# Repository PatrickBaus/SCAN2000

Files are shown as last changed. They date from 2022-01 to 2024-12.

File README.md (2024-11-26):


# Keithley 2000-SCAN SSR Replacement

This repository contains the KiCAD PCB project files for a [Keithley Model 2000-SCAN](https://download.tek.com/manual/2000SCAN-901-01_F-Jan-2014.pdf) replacement card. It uses solid-state relays instead of mechanical relays. See [below](#introduction) for a list of compatible devices. The design files can be found on the [releases](../../releases) page.

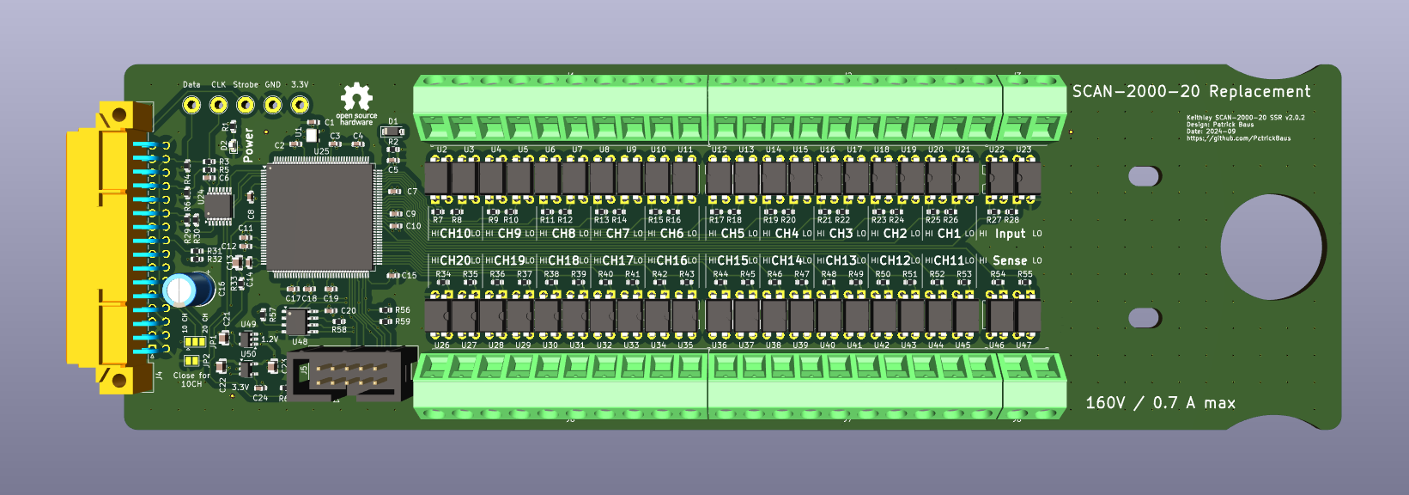
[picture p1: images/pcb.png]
SCAN2000 board


## Contents
- [Introduction](#introduction)
- [Design Files](#design-files)
- [Installation](#installation)
- [Accesories](#accesories)
- [Related Repositories](#related-repositories)
- [Versioning](#versioning)
- [License](#license)

## Introduction
The design is the successor of the SCAN2000 STM32 board previously released as [v1.x](https://github.com/PatrickBaus/SCAN2000/tree/v1). Instead of an STM32 microcontroller it uses an [iCE40](https://www.latticesemi.com/iCE40) FPGA to emulate the shift registers found on the 10 channel [Model 2000-SCAN](https://download.tek.com/manual/2000SCAN-901-01_F-Jan-2014.pdf) card and is also capable of decoding the protcol used by the 20-channel [Model 2000-SCAN-20](https://download.tek.com/manual/2000-20-901-01C_Jul2003_Instruction.pdf). The advantage of the FPGA is that the shift registers are implemented in hardware. The protocol spoken by the 10 channnel card requires freezing 24 bits clocked in _before_ the strobe bin is triggered, similar to the positive lookahead assertion of a [regular expression](https://en.wikipedia.org/wiki/Regular_expression). This is in stark contrast to typical protocols used by microcontrollers like, for example, [SPI](https://en.wikipedia.org/wiki/Serial_Peripheral_Interface) that uses a [chip select](https://en.wikipedia.org/wiki/Chip_select) control line to announce incoming data arriving _after_ the CS signal. A more detailed analysis of the problem can be found in the [doc/](doc/) folder.

The card was tested in a [Keithley DMM6500](https://www.tek.com/en/products/keithley/digital-multimeter/dmm6500) and a [Keithley Model 2002](https://www.tek.com/en/products/keithley/digital-multimeter/2002-series) in both configurations as a 10 channel and 20 channel card. The more recent [Keithley DMM6500](https://www.tek.com/en/products/keithley/digital-multimeter/dmm6500) supports both the older 10 channel [Model 2000-SCAN](https://download.tek.com/manual/2000SCAN-901-01_F-Jan-2014.pdf) and the newer [Model 2000-SCAN-20](https://download.tek.com/manual/2000-20-901-01C_Jul2003_Instruction.pdf) 20 channel scanner card. The same goes for the [Model 2000](https://www.tek.com/en/products/keithley/digital-multimeter/keithley-2000-series-6-digit-multimeter-scanning) and Model 2000-20. The Model 2000-20 is similar to the [Model 2000](https://www.tek.com/en/products/keithley/digital-multimeter/keithley-2000-series-6-digit-multimeter-scanning), but has a different firmware. The latest firmare of the [Model 2000](https://www.tek.com/en/products/keithley/digital-multimeter/keithley-2000-series-6-digit-multimeter-scanning) seems to support the 20 channel cards as well as suggested [here](https://www.eevblog.com/forum/circuit-studio/example-project-20-channel-solid-state-scan-card-for-k2000-dmm/msg3101128/#msg3101128). The [Model 2002](https://www.tek.com/en/products/keithley/digital-multimeter/2002-series) only supports 10 channel cards.

|DMM|Tested|Note|
|--|--|--|
|[DMM6500](https://www.tek.com/en/products/keithley/digital-multimeter/dmm6500)|:heavy_check_mark:|Works.|
|[2000](https://www.tek.com/en/products/keithley/digital-multimeter/keithley-2000-series-6-digit-multimeter-scanning)|:x:|Not tested, but should work. The latest firmware seems to support [20 channels](https://www.eevblog.com/forum/circuit-studio/example-project-20-channel-solid-state-scan-card-for-k2000-dmm/msg3101128/#msg3101128).|
|[2000-20](https://www.tek.com/en/products/keithley/digital-multimeter/keithley-2000-series-6-digit-multimeter-scanning)|:x:|Not tested, but should work.|
|[2010](https://www.tek.com/en/products/keithley/digital-multimeter/2010-series)|:heavy_check_mark:|Works, but only 10 channels cards are supported by the firmware.|
|[2001](https://www.tek.com/en/products/keithley/digital-multimeter/2001-series)|:x:|Not tested, but should work.|
|[2002](https://www.tek.com/en/products/keithley/digital-multimeter/2002-series)|:heavy_check_mark:|Works. Only 10 channels supported.|

## Design Files
The root folder contains the KiCAD files. The bill of materials can be found on the [releases](../../releases) page along with Gerber files for production.

## Installation
The source code for the FPGA and the installation instructions for the firmware can be found [here](https://github.com/PatrickBaus/SCAN2000_iCE40_Firmware). The FPGA source code must be written to the onboard SPI flash chip. One way to do so is to use an USB to SPI converter with an FT232H chip.

The SCAN2000 SSR board has two solder jumpers, ```JP1``` and ```JP2```. To enable only 10 channels close ```JP2``` and connect the two left pads of ```JP1``` together using a soldering iron. To enable 20 channel operation, leave ```JP2``` open and connect the two rightmost pads of ```JP1```.

The assembled card can then wired up and simply inserted into the multimeter. It will be supplied by the DMM through the Molex connector. To connect the scanner outputs to the, connect the screw terminals labeled ```Input``` to the DMM terminals labeled ```Input```. The same goes for the ```Sense``` terminals if operating in 4-wire mode.

## Accesories
The [Model 2000-SCAN](https://download.tek.com/manual/2000SCAN-901-01_F-Jan-2014.pdf) comes with four 10″ connectors that have a right angle 4 mm connector on one side and a tinned wire on the other. They are sold by Keithley as [CA-109A](https://download.tek.com/document/1KW-50660-1_Keithley_Test_Leads_Probes_Selector_Guide_100622.pdf) and are made by Mueller Electric. Their part numbers are [BU-0062-N-108-2 (red)](https://www.muellerelectric.com/products/bu-0062-n-108-2) and [BU-0062-N-108-0 (black)](https://www.muellerelectric.com/products/bu-0062-n-108-0). Keithley shortens the Mueller Electric parts to 10″. The same length is fine for this board as well.

## Related Repositories
See the following repositories for more information as these are part of the [design files](#design-files).

- [KiCad footprints](https://github.com/PatrickBaus/footprints.pretty)
- [KiCAD 3D models](https://github.com/PatrickBaus/footprints.3dshapes)
- [KiCAD schematic libraries](https://github.com/PatrickBaus/KiCad-libraries)

## Versioning
I use [SemVer](http://semver.org/) for versioning. For the versions available, see the [tags](../../tags) available for this repository.

- MAJOR versions in this context mean a breaking change to the external interface of the hardware like different connectors or functions.
- MINOR versions contain changes to the hardware that only affect the inner workings of the circuit, but otherwise the performance is unaffected.
- PATCH versions do not affect the schematics or invalidate older bill of materials. These changes may include updated components (to replace obsolete parts for example), an updated silkscreen, or fixed typos.

## License
This work is released under the CERN-OHL-W
See [https://ohwr.org/cern_ohl_w_v2.pdf](https://ohwr.org/cern_ohl_w_v2.pdf) or the included LICENSE file for more information.

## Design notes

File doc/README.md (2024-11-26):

# Keithley Model 2000-SCAN Serial Protocol
There are two versions of the scanner cards made by Keithley for their range of DMMs which are discussed here, the [Model 2000-SCAN](https://download.tek.com/manual/2000SCAN-901-01_F-Jan-2014.pdf) and the newer [Model 2000-SCAN-20](https://download.tek.com/manual/2000-20-901-01C_Jul2003_Instruction.pdf). Additionally there are the [Model 2001-SCAN](https://download.tek.com/manual/2001_SCAN_901_01C.pdf) and [Model 2001-TCSCAN](https://download.tek.com/manual/2001-TCSCAN-900-01A_April_2018.pdf). Both are 10 channel cards as well. The [Model 2001-SCAN](https://download.tek.com/manual/2001_SCAN_901_01C.pdf) has 8 relays and 2 SSRs for high speed multiplexing. The [Model 2001-TCSCAN](https://download.tek.com/manual/2001-TCSCAN-900-01A_April_2018.pdf) on the other hand has 9 channels and one reference junction for cold-junction compensated temperature measurements. The latter two will not be discussed here.

## Contents
- [Introduction](#introduction)
- [Model 2000-SCAN](#model-2000-scan)
- [Model 2000-SCAN-20](#model-2000-scan-20)
- [Exploring the Data Captures](#exploring-the-data-captures)

## Introduction
The schematics of the [Model 2000-SCAN](https://download.tek.com/manual/2000SCAN-901-01_F-Jan-2014.pdf) and the [Model 2000-SCAN-20](https://download.tek.com/manual/2000-20-901-01C_Jul2003_Instruction.pdf) cards can both be found online. Do note that the latest version of the Model 2000-SCAN manual found on the Tektronix website does not contain the schematics any more. The last revision to contain them was Revision D from April 1999. Use a search engine to find it.

The ```Model 2000-SCAN``` and the ```Model 2000-SCAN-20``` use two different serial protocols. These were recorded for different multimeters with a [R&S RTH1004](https://www.rohde-schwarz.com/us/products/test-and-measurement/oscilloscopes/rs-scope-rider-handheld-oscilloscope_63493-156160.html) using its digital inputs. Additionally, different types of multimeters use different clock timings, which will also be discussed below.

## Model 2000-SCAN
The ```Model 2000-SCAN``` is the older 10 channel version of the scanner card and it works with all types of DMMs. The examples shown below were recorded with a [DMM6500](https://www.tek.com/en/products/keithley/digital-multimeter/dmm6500) and a [Model 2002](https://www.tek.com/en/products/keithley/digital-multimeter/2002-series) as the host machine.

### Commands
The data communication between the card and the host device requires three data lines. The ```CLK``` line (recorded on channel ```D0```), the ```DATA``` line (```D2```) and a ```LATCH```/```STROBE``` line (```D1```). For the 10 channel card the DMM transfers 2 blocks of 3 bytes of data. It pulls the ```LATCH``` line ```high``` after each block. The first block sets or unsets all relays as required, the second block turns off the relay coils. In case of the [Model 2002](https://www.tek.com/en/products/keithley/digital-multimeter/2002-series) the ```CLK``` and ```DATA``` line idle ```high``` and only the ```LATCH``` line idles ```low```.
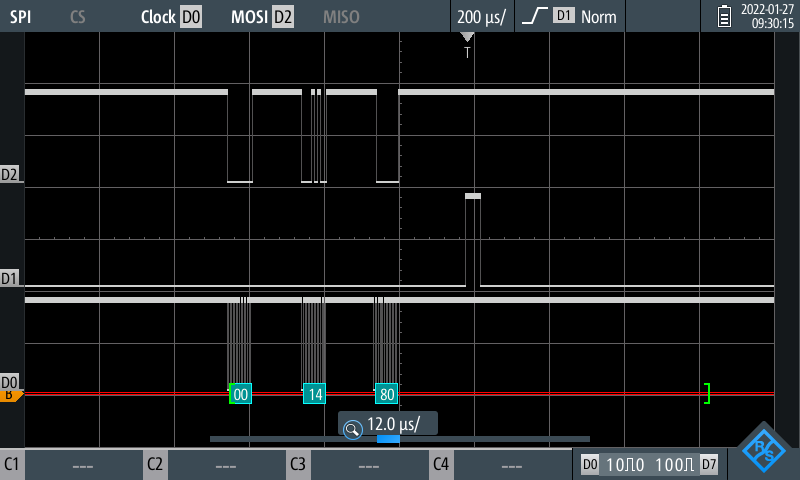
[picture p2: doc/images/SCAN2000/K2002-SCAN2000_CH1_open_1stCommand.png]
Model 2000-SCAN DMM6500 opening CH1


The [DMM6500](https://www.tek.com/en/products/keithley/digital-multimeter/dmm6500) uses a different scheme where all data lines idle ```low``` as can be seen here.
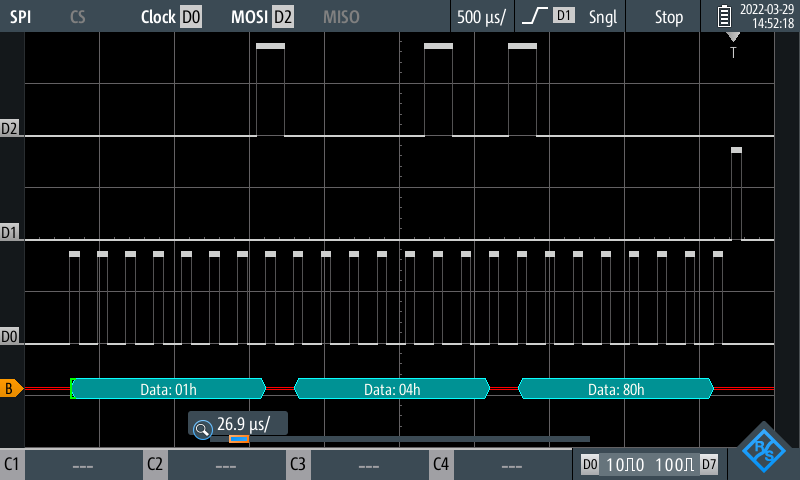
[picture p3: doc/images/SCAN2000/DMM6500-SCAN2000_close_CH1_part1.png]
Model 2000-SCAN DMM6500 closing CH1


The protocol itself is a series bits where each bit correspondes to a relay coil either being turned on or off. This is due to the nature of the 2-coil latching relays (```Panasonic TQ2E-L2-5V```). Each of those coils is responsible for either closing the relay or opening it. 10 relays plus 1 relay to switch between 4W mode and 2W mode requires 22 bits to control, hence two fewer than the 24 bits sent.

The decoded protocol is shown here and can also verified using the schematic schown in the manual.

```mermaid
---
title: "2000-SCAN protocol"
---
packet-beta
0: "7⮝"
1: "8⮟"
2: "8⮝"
3: "9⮟"
4: "9⮝"
5: "10⮝"
6: "10⮟"
7: "X"
8: "5⮝"
9: "5⮟"
10: "X"
11: "4W⮟"
12: "4W⮝"
13: "6⮟"
14: "6⮝"
15: "7⮟"
16: "1⮟"
17: "1⮝"
18: "2⮟"
19: "2⮝"
20: "3⮟"
21: "3⮝"
22: "4⮟"
23: "4⮝"
```

```⮟``` means closing the channel, ```⮝``` means opening the channel, ```X``` means do-not-care bit. The do-not-care bits have no meaning as those pins of the latches on the PCB are not connected. See pin Q8 of U101 (bit 7) and pin Q3 of U102 (bit 10). The do-not-care bits are typically set, but this is not required by the hardware.

As mentioned above, once the relay configuration is sent, the DMM then sends a series of zeroes to turn off the current to the relay coils. The [Model 2002](https://www.tek.com/en/products/keithley/digital-multimeter/2002-series) waits roughly ```2.8 ms``` between the datablock blocks

![Model 2000-SCAN K2002 timing between data blocks](images/SCAN2000/K2002-SCAN2000_command_interval.png)

while the [DMM6500](https://www.tek.com/en/products/keithley/digital-multimeter/dmm6500) waits ```3.8 ms``` for the relay to actuate.

![Model 2000-SCAN DMM6500 timing between data blocks](images/SCAN2000/DMM6500-SCAN2000_command_interval.png)

### Clock Speed
The most striking difference between the [DMM6500](https://www.tek.com/en/products/keithley/digital-multimeter/dmm6500) and the [Model 2002](https://www.tek.com/en/products/keithley/digital-multimeter/2002-series) is the data rate at which the signals are transferred. The clock frequency used by the [Model 2002](https://www.tek.com/en/products/keithley/digital-multimeter/2002-series) is ```2 MHz```

![Model 2000-SCAN K2002 SCLK frequency](images/SCAN2000/K2002-SCAN2000_CLK_timing.png)

while the  [DMM6500](https://www.tek.com/en/products/keithley/digital-multimeter/dmm6500) uses a clock speed of ```100 kHz```

![Model 2000-SCAN DMM6500 SCLK frequency](images/SCAN2000/DMM6500_CLK_timing.png)

The reason for the faster clock of the [Model 2002](https://www.tek.com/en/products/keithley/digital-multimeter/2002-series) is simple. The bus of the [Model 2002](https://www.tek.com/en/products/keithley/digital-multimeter/2002-series) is used by multiple devices all talking on the same wire, which can be seen here:

![Model 2000-SCAN K2002 second device sending data](images/SCAN2000/K2002-SCAN2000_2commands_second_transmitter_all_annotated.png)

In yellow there is a data packet for another device being transferred on the bus (```D0``` and ```D2```), but there is no ```LATCH``` line (```D1```) activity. Later there more data packets coming in and circled in red the two ```LATCH``` signals (```D1```) can be seen. There are are at least two more devices active on that bus. One transfers at ```1 MHz``` clock speed

![Model 2000-SCAN K2002 clockspeed of the  second device](images/SCAN2000/K2002-SCAN2000_CLK_timing_second_transmitter.png)

The other one is even slower and shows up as seemingly rogue bits on the ```CLK```/```D0``` line.

![Model 2000-SCAN K2002 additional devices on the bus](images/SCAN2000/K2002-SCAN2000_second_transmitter.png)

The image above shows both of the two other devices on the bus. There is activity on the ```CLK```/```D0``` line with two different clock intervals. The lone pulse on the right side is the slow third device. This third device is the reason why using a standard microcontroller is not possible, like in [v1.x](https://github.com/PatrickBaus/SCAN2000/tree/v1) of the scanner card that used an STM32 microcontroller. MCUs are aligned to a fixed number of clock cycles when reading a bus using their hardware peripherals. The extra clock pulse of the slow transmitter causes the hardware controller to desync at random intervals. Sampling the bus in software instead of the hardware interface is not feasable as well as the bus too fast at ```2 MHz```. Using the latches of the original Keithley design, this is not a problem, as the last 24 bits before a ```LATCH``` signal comes in are stored in the latch. Using an FPGA for this design allows to mimic the latches while allowing to switch between the [Model 2000-SCAN protocol](#commands) and the [Model 2000-SCAN-20 protocol](#commands-1) without changing the hardware.

## Model 2000-SCAN-20
The [Model 2000-SCAN-20](https://download.tek.com/manual/2000-20-901-01C_Jul2003_Instruction.pdf) is a more modern card which is only supported by the latest firmware of the [Model 2000](https://www.tek.com/en/products/keithley/digital-multimeter/keithley-2000-series-6-digit-multimeter-scanning) DMM and the [DMM6500](https://www.tek.com/en/products/keithley/digital-multimeter/dmm6500). The examples shown below were recorded with a [DMM6500](https://www.tek.com/en/products/keithley/digital-multimeter/dmm6500) as the host machine.

### Commands
The data communication also requires three data lines like the 10-channel card. The ```CLK``` line (```D0```), the ```DATA``` line (```D2```) and a ```LATCH```/```STROBE``` line (```D1```). The protocol is a bit more straight forward, even bits disconnect the relay, odd bits connect the relay. The 20 relays plus 1 relay for the 4W mode require 42 bits. This is being sent as 6 bytes.

```mermaid
---
title: "2000-SCAN-20 protocol"
---
packet-beta
0-1: "11"
2-3: "12"
4-5: "13"
6-7: "14"
8-9: "15"
10-11: "16"
12-13: "17"
14-15: "18"
16-17: "19"
18-19: "20"
20-21: "1"
22-23: "2"
24-25: "3"
26-27: "4"
28-29: "5"
30-31: "6"
32-33: "7"
34-35: "8"
36-37: "9"
38-39: "10"
40-41: "4W"
42-47: "X"
```

For example closing CH1 is sent as two blocks of ```0x00``` ```0x00``` ```0x00``` ```0x20``` ```0x00``` ```0x00``` (bit 21 is set) and ```0x00``` ```0x00``` ```0x00``` ```0x00``` ```0x00``` ```0x00```. The second block turns all relay coils off as discussed above.

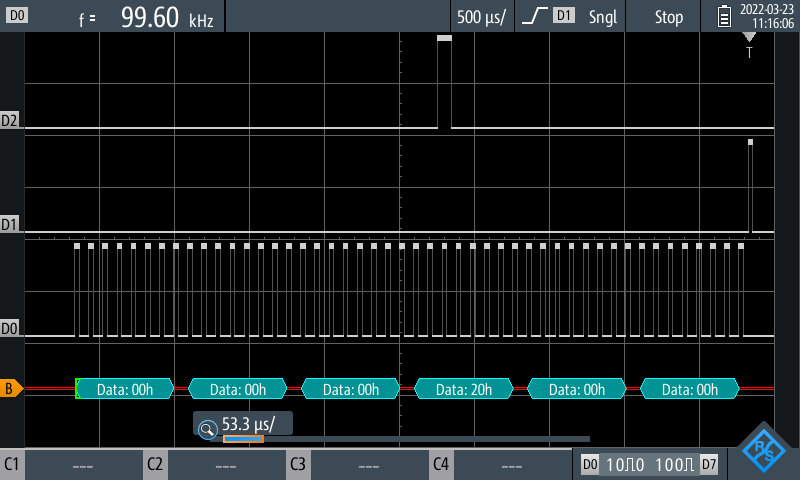
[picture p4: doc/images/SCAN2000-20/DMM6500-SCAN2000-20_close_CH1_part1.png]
Model 2000-SCAN-20 DMM6500 closing CH1, first block
 and

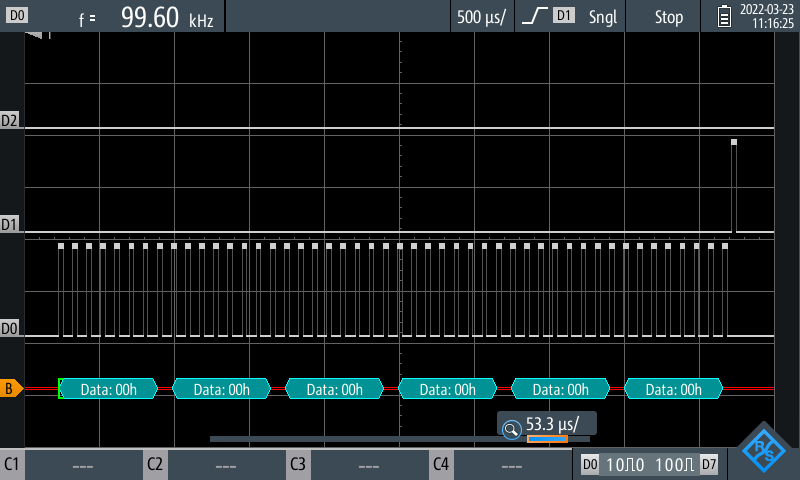
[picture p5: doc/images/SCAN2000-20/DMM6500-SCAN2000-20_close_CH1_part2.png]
Model 2000-SCAN-20 DMM6500 closing CH1, second block


The second block is sent after a delay of ```3.8 ms```.

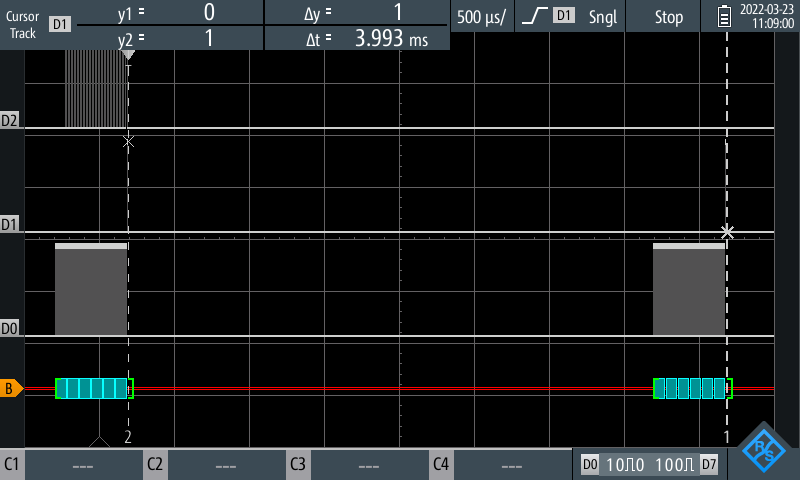
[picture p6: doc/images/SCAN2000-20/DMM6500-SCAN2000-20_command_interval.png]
Model 2000-SCAN-20 DMM6500 timing between data blocks


### Clock Speed
The [DMM6500](https://www.tek.com/en/products/keithley/digital-multimeter/dmm6500) clocks this bus at ```100 kHz``` just like the 10-channel version.

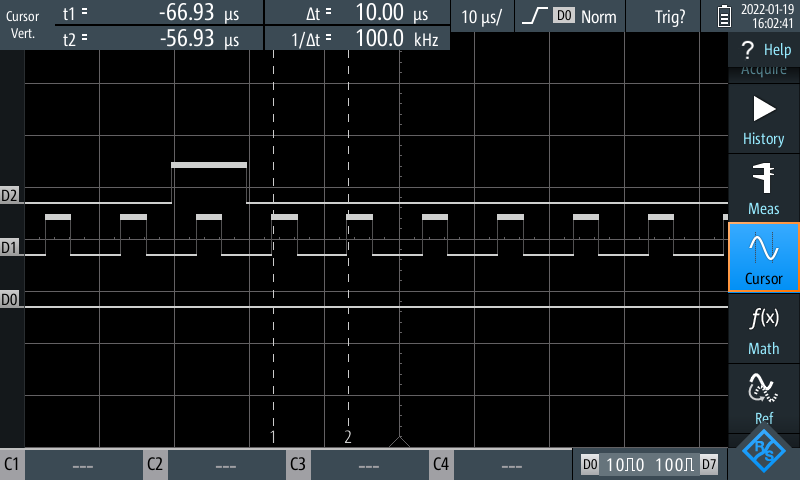
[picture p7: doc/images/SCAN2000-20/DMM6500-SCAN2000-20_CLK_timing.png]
Model 2000-SCAN-20 DMM6500 SCLK frequency


Do note, the ```CLK``` line is input channel ```D1``` and ```STROBE``` is ```D1``` in this capture.

## Exploring the Data Captures
This repository not only provides screen captures, but also the raw data obtained using the [R&S RTH1004](https://www.rohde-schwarz.com/us/products/test-and-measurement/oscilloscopes/rs-scope-rider-handheld-oscilloscope_63493-156160.html). This data can be found in the [plots/](plots/) directory as [csv files](https://en.wikipedia.org/wiki/Comma-separated_values) and can be plotted using your own plotter or the example [Python Matplotlib](https://matplotlib.org/) [script](plots/plotter.py) provided. This section shows how to install the script.

### Installing Dependencies
These instructions assume a Linux Bash shell and Python already installed on the system. Type or copy the following commands into a shell in the [doc/plots/](plots/) directory.

```bash
python -m venv env/
source env/bin/activate
pip install - r requirements.txt
```

### Running the Script
The plot script can now be executed using the following commands run inside the [doc/plots/](plots/) directory
```bash
source env/bin/activate
./plotter.py <plot_file>
```

The `source env/bin/activate` line can omitted if the virtual environment has already been activated. The ```<plot_file>``` must be any of the Python files provided in the [doc/plots/SCAN2000](plots/SCAN2000) or [doc/plots/SCAN2000-20](plots/SCAN2000-20) subdirectories, for example
```bash
./plotter.py SCAN2000/K2002-SCAN2000_commands_and_second_transmitter.py
```

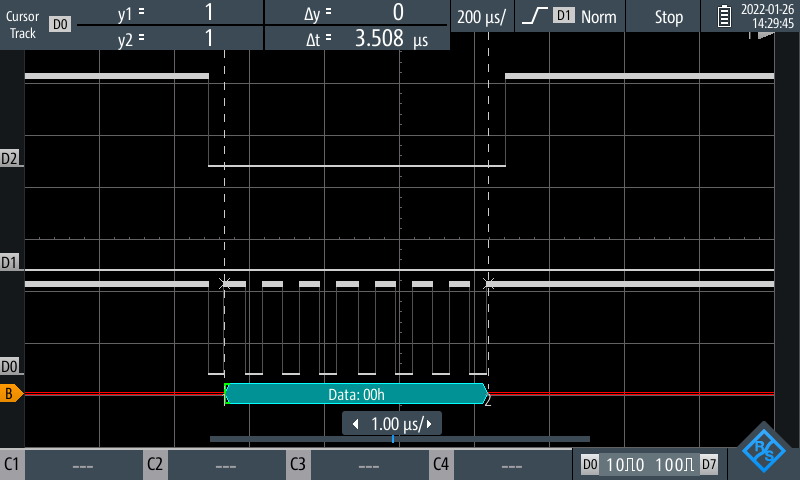
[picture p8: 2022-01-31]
doc/images/SCAN2000/K2002-SCAN2000_CLK_timing.png

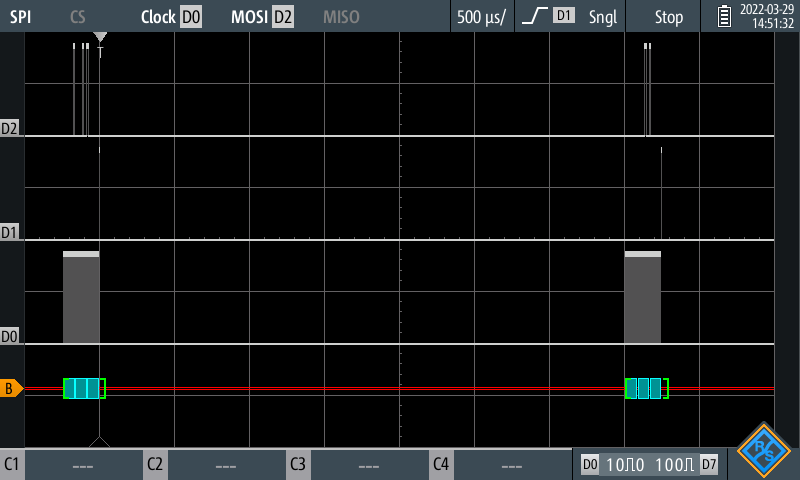
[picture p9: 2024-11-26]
doc/images/SCAN2000/DMM6500-SCAN2000_close_CH1.png

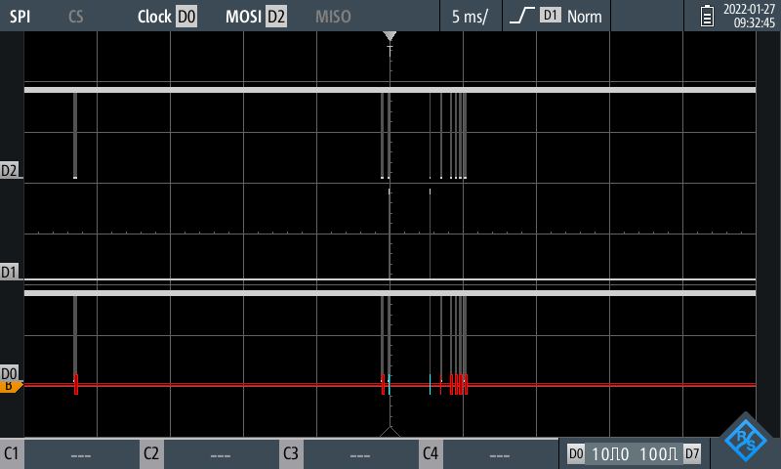
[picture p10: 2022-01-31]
doc/images/SCAN2000/K2002-SCAN2000_2commands_second_transmitter_all.png

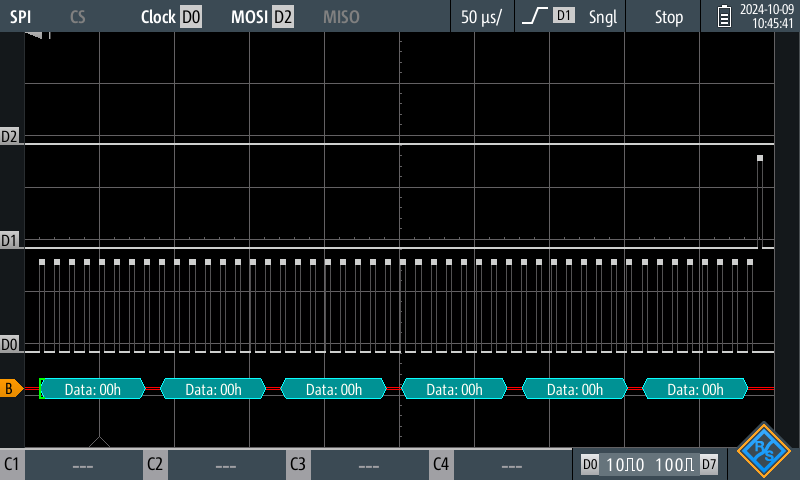
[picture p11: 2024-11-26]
doc/images/SCAN2000-20/DMM6500-SCAN2000-20_close_CH2_4W_part2.png

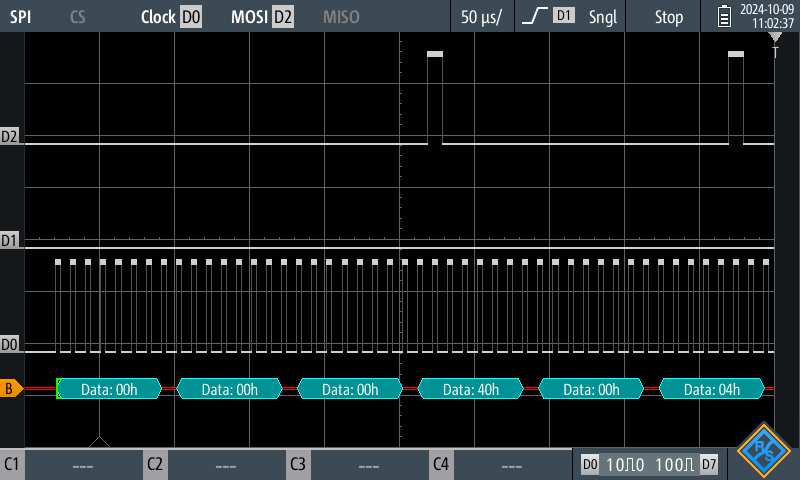
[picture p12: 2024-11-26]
doc/images/SCAN2000-20/DMM6500-SCAN2000-20_open_CH2_4W_close_CH10_4W_part1.png

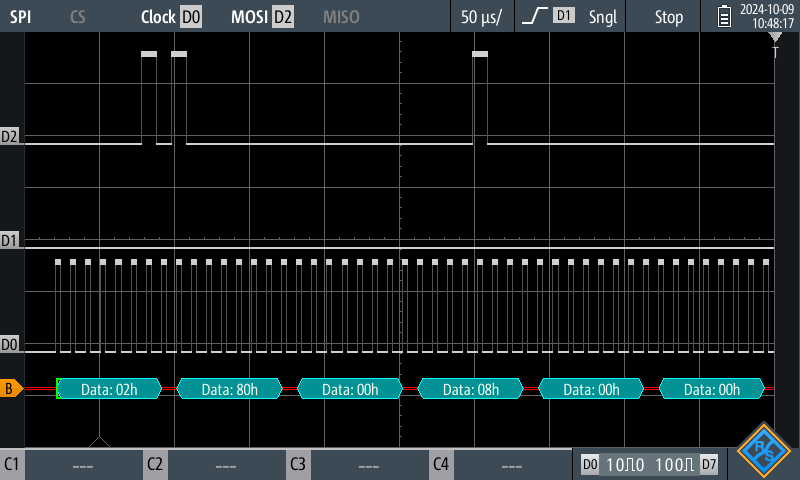
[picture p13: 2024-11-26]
doc/images/SCAN2000-20/DMM6500-SCAN2000-20_close_CH10_4W_part1.png

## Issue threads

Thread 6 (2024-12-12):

### ISSUE TITLE
2.0.2 Gerber archive doesn't contain internal layers

### ISSUE THREAD

**Issue by reykada** [PatrickBaus/SCAN2000#6]
I just realized it after 2-layer PCBs ordered and arrived when I started to assembly, luckily only FPGA and few capacitors were soldered only.

**Comment by PatrickBaus** [comment]
Oh, you are absolutely right. I am so sorry. I have added the missing layers to the CI and will release a new version immediately.

**Comment by reykada** [comment]
No worries, I had to check it myself before order PCBs. Thank you for the quick fix!

**Comment by PatrickBaus** [comment]
I have published version 2.0.3. As soon as the CI has built the files it should be available.

**Comment by reykada** [comment]
Cool, thanks for sharing the project!

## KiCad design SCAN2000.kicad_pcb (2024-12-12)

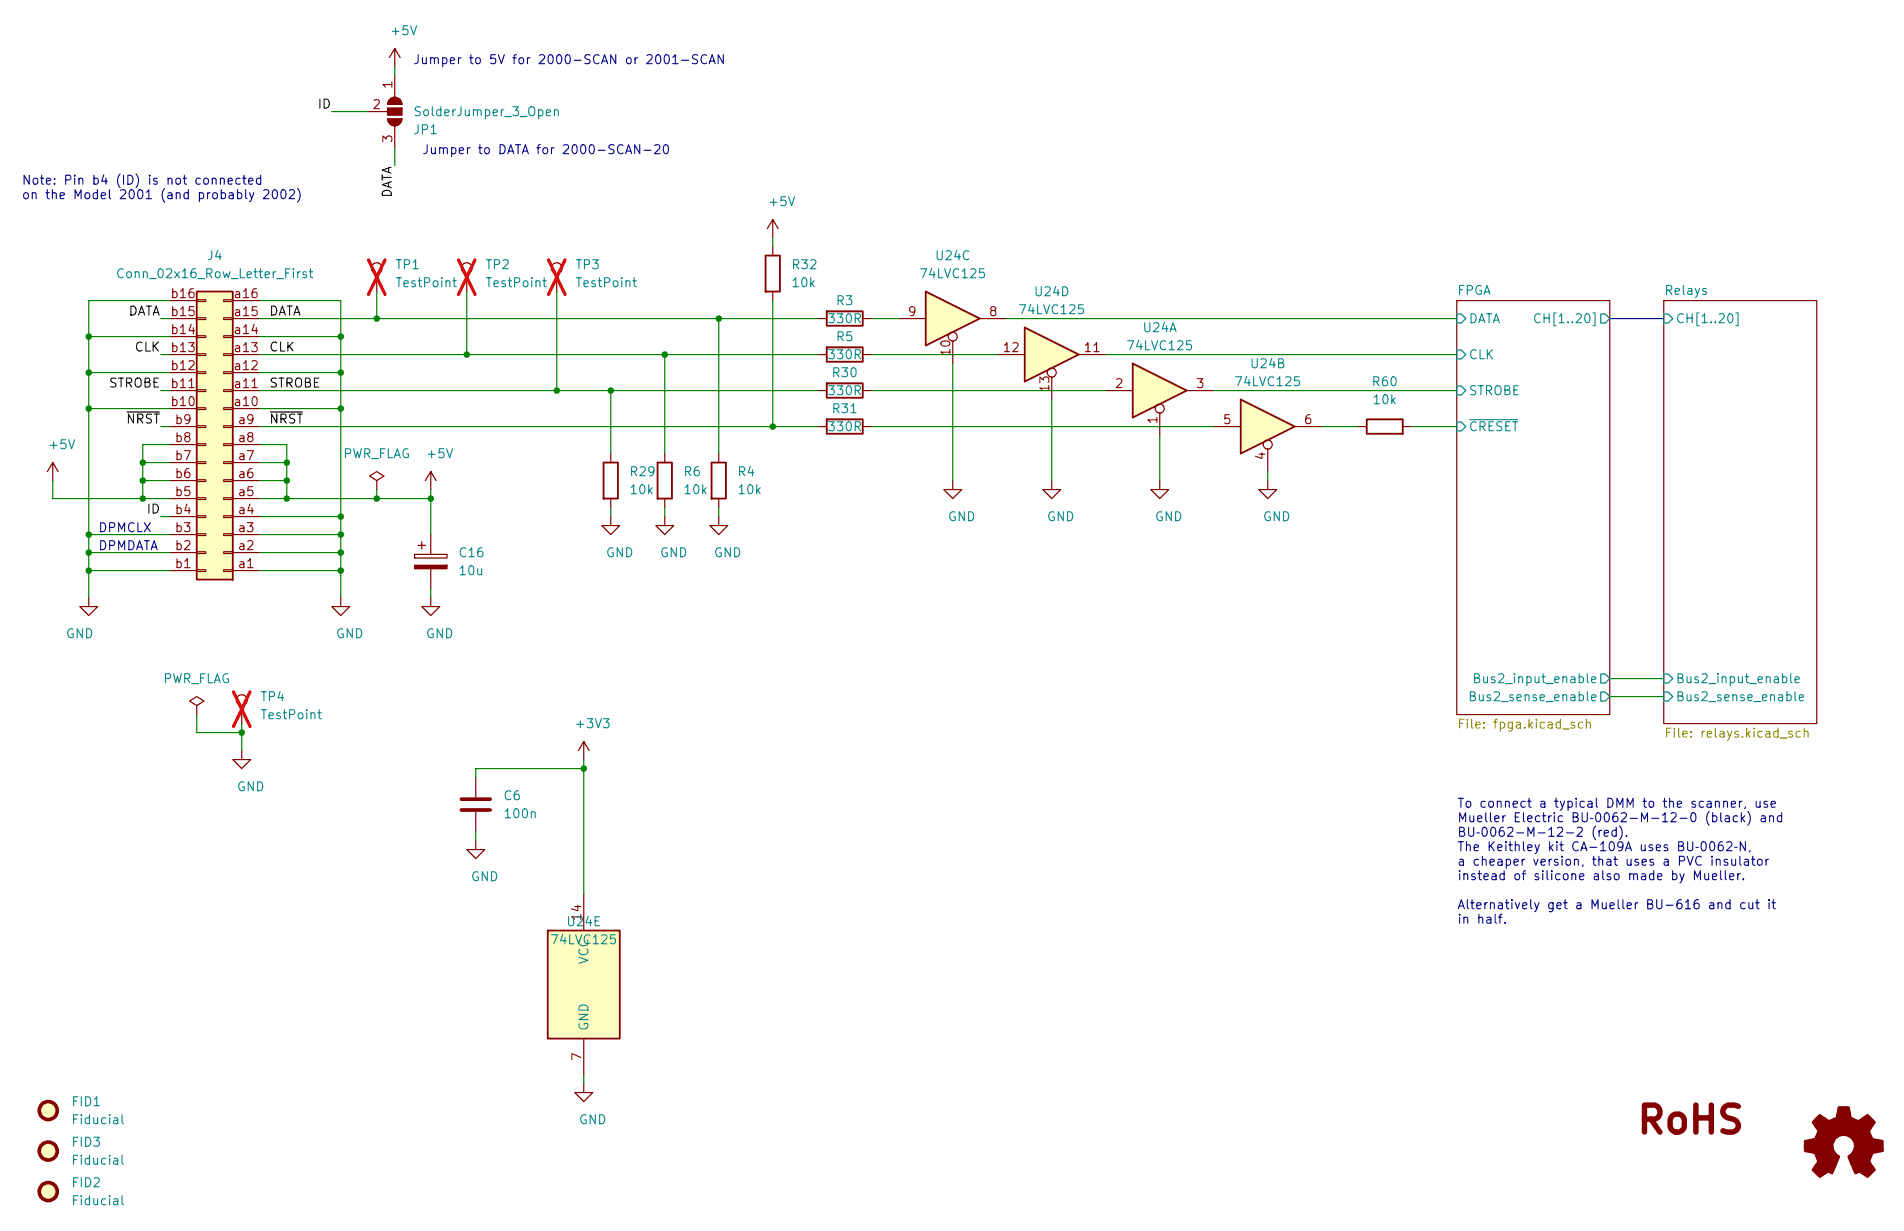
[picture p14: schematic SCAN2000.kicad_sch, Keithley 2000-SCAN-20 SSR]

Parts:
C6: 100n; C_0603_1608Metric
C16: 10u; CP_Radial_D6.3mm_P2.50mm
FID1, FID2, FID3: Fiducial; Fiducial_0.5mm_Mask1mm
J4: Conn_02x16_Row_Letter_First; DIN41612_B2_2x16_Male_Horizontal_THT; Digikey# 09272326804-ND
JP1: SolderJumper_3_Open; SolderJumper-3_P1.3mm_Open_Pad1.0x1.5mm
LOGO1: Logo_Open_Hardware_Small; OSHW-Logo_7.5x8mm_SilkScreen
R3, R5, R30, R31: 330R; R_0603_1608Metric
R4, R6, R29, R32, R60: 10k; R_0603_1608Metric
TP1, TP2, TP3, TP4: TestPoint; TestPoint_Loop_D2.60mm_Drill1.6mm_Beaded; not fitted
U24: 74LVC125; TSSOP-14_4.4x5mm_P0.65mm

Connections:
+3V3: C6.1, U24.14 (VCC); also elsewhere on the board
+5V: C16.1, J4.a5, J4.a6, J4.a7, J4.a8, J4.b5, J4.b6, J4.b7, J4.b8, JP1.1 (A), R32.1; also elsewhere on the board
/CLK: J4.a13, J4.b13, R5.2, R6.1, TP2.1
/DATA: J4.a15, J4.b15, JP1.3 (B), R3.2, R4.1, TP1.1
/FPGA/CLK: U24.11; also elsewhere on the board
/FPGA/DATA: U24.8; also elsewhere on the board
/FPGA/STROBE: U24.3; also elsewhere on the board
/FPGA/~CRESET: R60.2; also elsewhere on the board
/ID: J4.b4, JP1.2 (C)
/STROBE: J4.a11, J4.b11, R29.1, R30.2, TP3.1
/~NRST: J4.a9, J4.b9, R31.2, R32.2
GND: C6.2, C16.2, J4.a1, J4.a2, J4.a3, J4.a4, J4.a10, J4.a12, J4.a14, J4.a16, J4.b1, J4.b2, J4.b3, J4.b10, J4.b12, J4.b14, J4.b16, R4.2, R6.2, R29.2, TP4.1, U24.1, U24.4, U24.7 (GND), U24.10, U24.13; also elsewhere on the board
unnamed: R3.1, U24.9
unnamed: R5.1, U24.12
unnamed: R30.1, U24.2
unnamed: R31.1, U24.5
unnamed: R60.1, U24.6

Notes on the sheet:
DPMDATA
DPMCLX
Jumper to 5V for 2000-SCAN or 2001-SCAN
Jumper to DATA for 2000-SCAN-20
To connect a typical DMM to the scanner, use Mueller Electric BU‐0062-M-12-0 (black) and BU‐0062-M-12-2 (red). The Keithley kit CA-109A uses BU‐0062‐N, a cheaper version, that uses a PVC insulator instead of silicone also made by Mueller. Alternatively get a Mueller BU-616 and cut it in half.
Note: Pin b4 (ID) is not connected on the Model 2001 (and probably 2002)

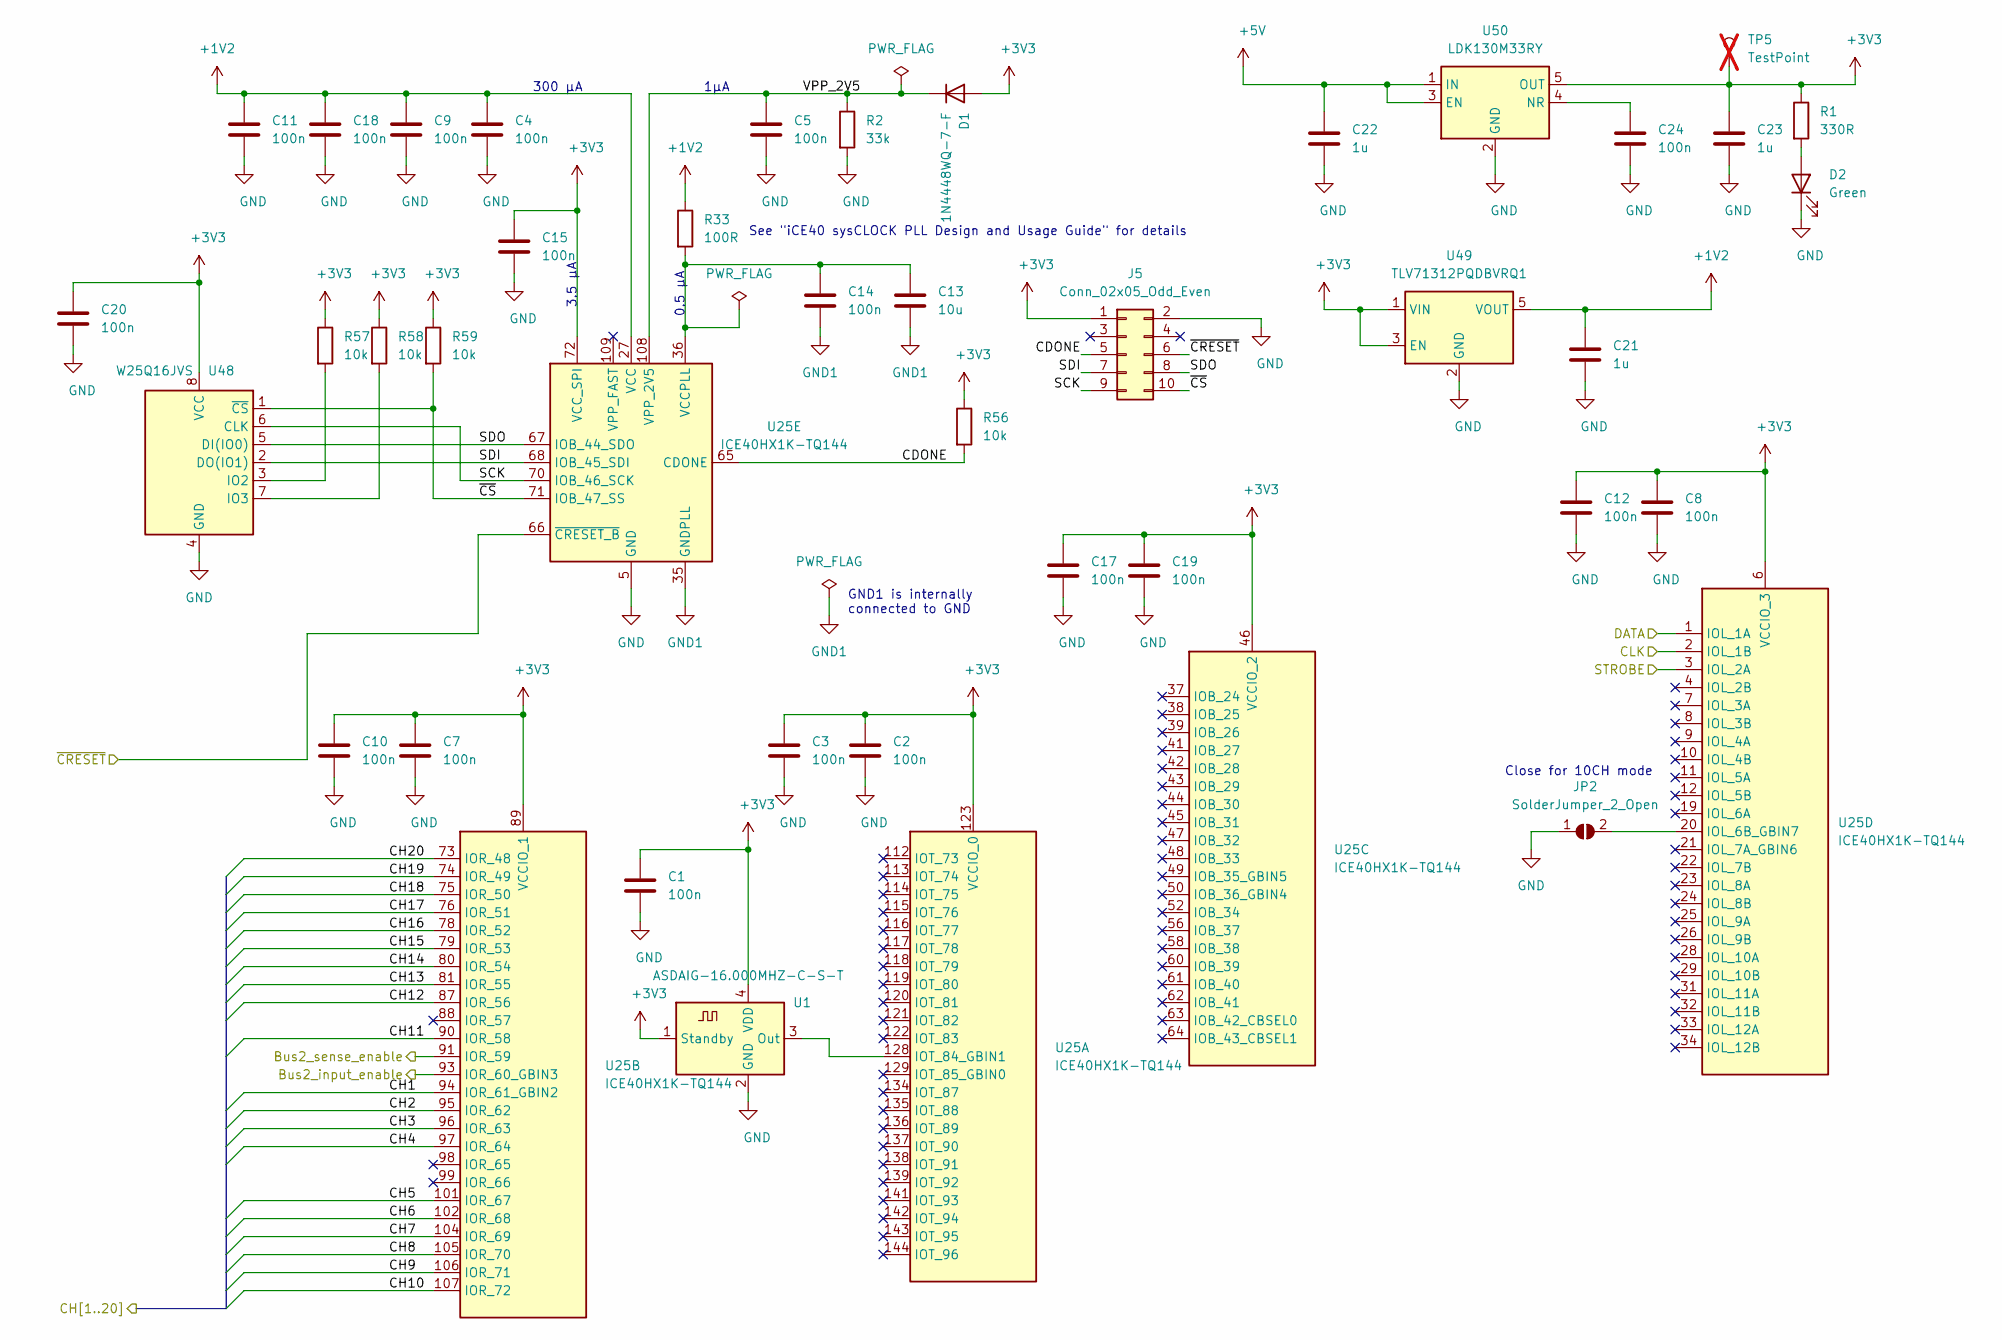
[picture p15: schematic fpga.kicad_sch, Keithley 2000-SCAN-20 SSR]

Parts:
C1, C2, C3, C4, C5, C7, C8, C9, C10, C11, C12, C14, C15, C17, C18, C19, C20, C24: 100n; C_0603_1608Metric
C13: 10u; C_0805_2012Metric
C21, C22, C23: 1u; C_0805_2012Metric
D1: 1N4448WQ-7-F; D_SOD-123
D2: Green; LED_0603_1608Metric
J5: Conn_02x05_Odd_Even; IDC-Header_2x05_P2.54mm_Vertical
JP2: SolderJumper_2_Open; SolderJumper-2_P1.3mm_Open_Pad1.0x1.5mm
R1: 330R; R_0603_1608Metric
R2: 33k; R_0603_1608Metric
R33: 100R; R_0603_1608Metric
R56, R57, R58, R59: 10k; R_0603_1608Metric
TP5: TestPoint; TestPoint_Loop_D2.60mm_Drill1.6mm_Beaded; not fitted
U1: ASDAIG-16.000MHZ-C-S-T; Oscillator_SMD_Abracon_ASDMB-4Pin_2.5x2.0mm
U25: ICE40HX1K-TQ144; TQFP-144_20x20mm_P0.5mm
U48: W25Q16JVS; SOIC-8_3.9x4.9mm_P1.27mm
U49: TLV71312PQDBVRQ1; SOT-23-5
U50: LDK130M33RY; SOT-23-5

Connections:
+1V2: C4.1, C9.1, C11.1, C18.1, C21.1, R33.1, U25.27 (VCC), U25.51 (VCC), U25.92 (VCC), U25.111 (VCC), U49.5 (VOUT)
+3V3: C1.1, C2.1, C3.1, C7.1, C8.1, C10.1, C12.1, C15.1, C17.1, C19.1, C20.1, C23.1, D1.2 (A), J5.1, R1.1, R56.1, R57.1, R58.1, R59.1, TP5.1, U1.1 (Standby), U1.4 (VDD), U25.6 (VCCIO_3), U25.30 (VCCIO_3), U25.46 (VCCIO_2), U25.57 (VCCIO_2), U25.72 (VCC_SPI), U25.89 (VCCIO_1), U25.100 (VCCIO_1), U25.123 (VCCIO_0), U25.133 (VCCIO_0), U48.8 (VCC), U49.1 (VIN), U49.3 (EN), U50.5 (OUT); also elsewhere on the board
+5V: C22.1, U50.1 (IN), U50.3 (EN); also elsewhere on the board
/FPGA/Bus2_input_enable: U25.93 (IOR_60_GBIN3); also elsewhere on the board
/FPGA/Bus2_sense_enable: U25.91 (IOR_59); also elsewhere on the board
/FPGA/CDONE: J5.5, R56.2, U25.65 (CDONE)
/FPGA/CH1: U25.94 (IOR_61_GBIN2); also elsewhere on the board
/FPGA/CH2: U25.95 (IOR_62); also elsewhere on the board
/FPGA/CH3: U25.96 (IOR_63); also elsewhere on the board
/FPGA/CH4: U25.97 (IOR_64); also elsewhere on the board
/FPGA/CH5: U25.101 (IOR_67); also elsewhere on the board
/FPGA/CH6: U25.102 (IOR_68); also elsewhere on the board
/FPGA/CH7: U25.104 (IOR_69); also elsewhere on the board
/FPGA/CH8: U25.105 (IOR_70); also elsewhere on the board
/FPGA/CH9: U25.106 (IOR_71); also elsewhere on the board
/FPGA/CH10: U25.107 (IOR_72); also elsewhere on the board
/FPGA/CH11: U25.90 (IOR_58); also elsewhere on the board
/FPGA/CH12: U25.87 (IOR_56); also elsewhere on the board
/FPGA/CH13: U25.81 (IOR_55); also elsewhere on the board
/FPGA/CH14: U25.80 (IOR_54); also elsewhere on the board
/FPGA/CH15: U25.79 (IOR_53); also elsewhere on the board
/FPGA/CH16: U25.78 (IOR_52); also elsewhere on the board
/FPGA/CH17: U25.76 (IOR_51); also elsewhere on the board
/FPGA/CH18: U25.75 (IOR_50); also elsewhere on the board
/FPGA/CH19: U25.74 (IOR_49); also elsewhere on the board
/FPGA/CH20: U25.73 (IOR_48); also elsewhere on the board
/FPGA/CLK: U25.2 (IOL_1B); also elsewhere on the board
/FPGA/DATA: U25.1 (IOL_1A); also elsewhere on the board
/FPGA/SCK: J5.9, U25.70 (IOB_46_SCK), U48.6 (CLK)
/FPGA/SDI: J5.7, U25.68 (IOB_45_SDI), U48.2 (DO(IO1))
/FPGA/SDO: J5.8, U25.67 (IOB_44_SDO), U48.5 (DI(IO0))
/FPGA/STROBE: U25.3 (IOL_2A); also elsewhere on the board
/FPGA/VPP_2V5: C5.1, D1.1 (K), R2.1, U25.108 (VPP_2V5)
/FPGA/~CRESET: J5.6, U25.66 (~CRESET_B); also elsewhere on the board
/FPGA/~CS: J5.10, R59.2, U25.71 (IOB_47_SS), U48.1 (~CS)
GND: C1.2, C2.2, C3.2, C4.2, C5.2, C7.2, C8.2, C9.2, C10.2, C11.2, C12.2, C15.2, C17.2, C18.2, C19.2, C20.2, C21.2, C22.2, C23.2, C24.2, D2.1 (K), J5.2, JP2.1 (A), R2.2, U1.2 (GND), U25.5 (GND), U25.13 (GND), U25.14 (GND), U25.59 (GND), U25.69 (GND), U25.86 (GND), U25.103 (GND), U25.132 (GND), U25.140 (GND), U48.4 (GND), U49.2 (GND), U50.2 (GND); also elsewhere on the board
GND1: C13.2, C14.2, U25.35 (GNDPLL)
unnamed: D2.2 (A), R1.2
unnamed: JP2.2 (B), U25.20 (IOL_6B_GBIN7)
unnamed: U1.3 (Out), U25.128 (IOT_84_GBIN1)
unnamed: C13.1, C14.1, R33.2, U25.36 (VCCPLL)
unnamed: R57.2, U48.3 (IO2)
unnamed: R58.2, U48.7 (IO3)
unnamed: C24.1, U50.4 (NR)

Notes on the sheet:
1µA
Close for 10CH mode
3.5 µA
See "iCE40 sysCLOCK PLL Design and Usage Guide" for details
300 µA
0.5 µA
GND1 is internally connected to GND

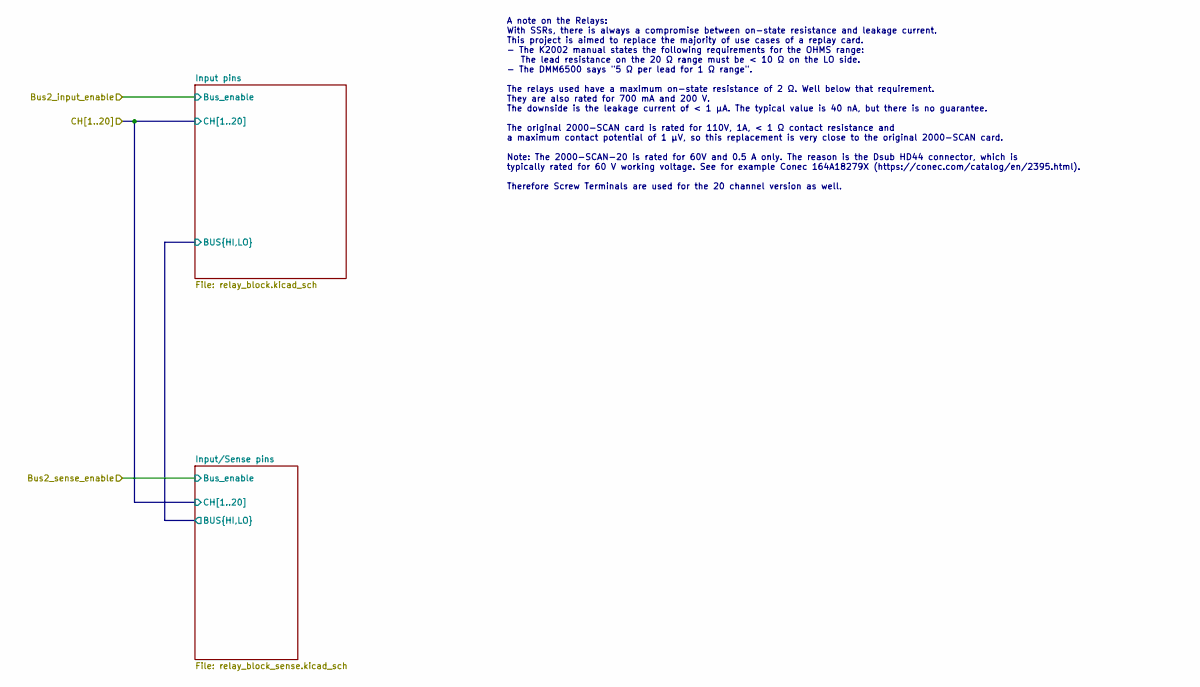
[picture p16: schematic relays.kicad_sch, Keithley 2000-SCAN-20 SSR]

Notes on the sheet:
A note on the Relays: With SSRs, there is always a compromise between on-state resistance and leakage current. This project is aimed to replace the majority of use cases of a replay card. - The K2002 manual states the following requirements for the OHMS range: The lead resistance on the 20 Ω range 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

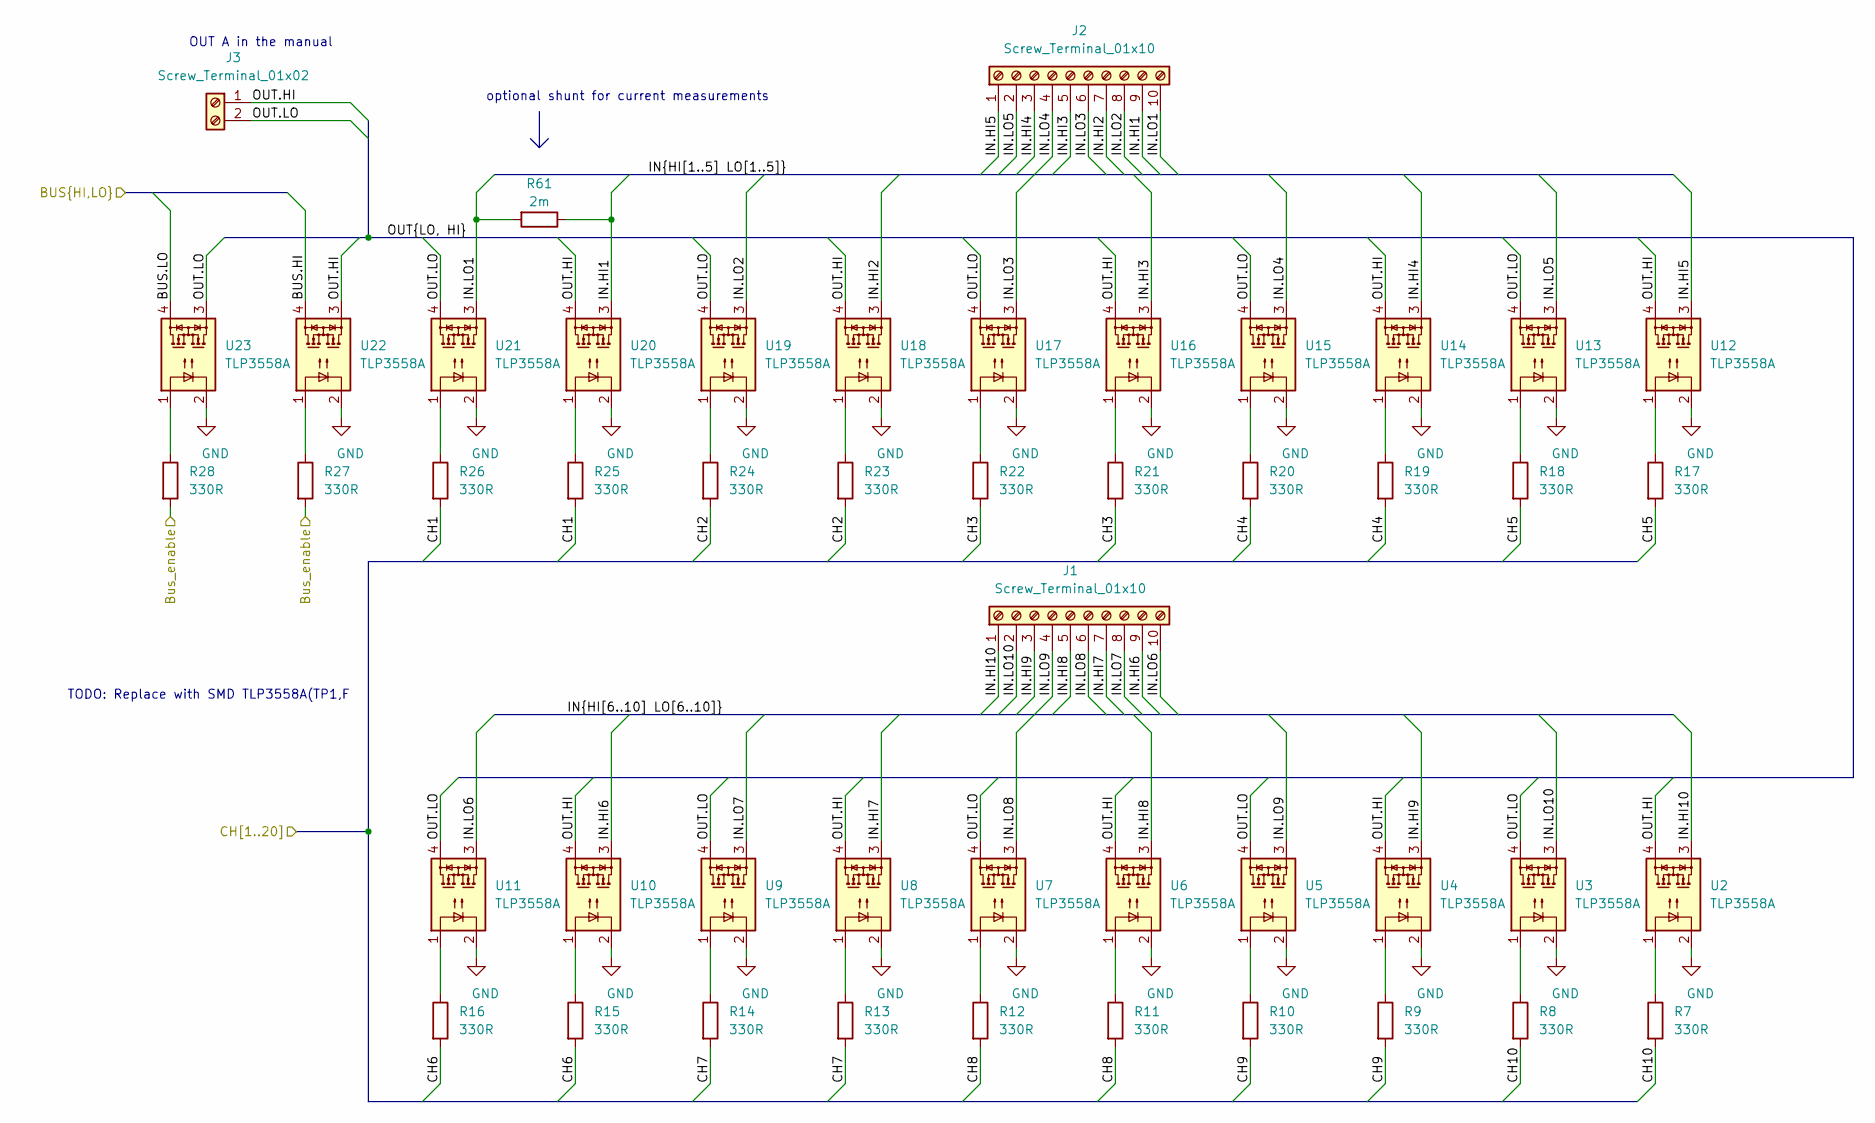
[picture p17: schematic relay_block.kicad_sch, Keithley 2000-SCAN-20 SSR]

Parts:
J1, J2: Screw_Terminal_01x10; TerminalBlock_Phoenix_SMKDSN-1,5-10-5.08_1x10_P5.08mm_Horiz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
J3: Screw_Terminal_01x02; TerminalBlock_Phoenix_SMKDSN-1,5-2-5.08_1x02_P5.08mm_Horizo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
R7, R8, R9, R10, R11, R12, R13, R14, R15, R16, R17, R18, R19, R20, R21, R22, R23, R24, R25, R26, R27, R28: 330R; R_0603_1608Metric
R61: 2m; R_2512_6332Metric
U2, U3, U4, U5, U6, U7, U8, U9, U10, U11, U12, U13, U14, U15, U16, U17, U18, U19, U20, U21, U22, U23: TLP3558A; DIP-4_W7.62mm

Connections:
/FPGA/Bus2_input_enable: R27.2, R28.2; also elsewhere on the board
/FPGA/CH1: R25.2, R26.2; also elsewhere on the board
/FPGA/CH2: R23.2, R24.2; also elsewhere on the board
/FPGA/CH3: R21.2, R22.2; also elsewhere on the board
/FPGA/CH4: R19.2, R20.2; also elsewhere on the board
/FPGA/CH5: R17.2, R18.2; also elsewhere on the board
/FPGA/CH6: R15.2, R16.2; also elsewhere on the board
/FPGA/CH7: R13.2, R14.2; also elsewhere on the board
/FPGA/CH8: R11.2, R12.2; also elsewhere on the board
/FPGA/CH9: R9.2, R10.2; also elsewhere on the board
/FPGA/CH10: R7.2, R8.2; also elsewhere on the board
/Relays/Input pins/BUS.HI: U22.4; also elsewhere on the board
/Relays/Input pins/BUS.LO: U23.4; also elsewhere on the board
/Relays/Input pins/IN.HI1: J2.9, R61.1, U20.3
/Relays/Input pins/IN.HI2: J2.7, U18.3
/Relays/Input pins/IN.HI3: J2.5, U16.3
/Relays/Input pins/IN.HI4: J2.3, U14.3
/Relays/Input pins/IN.HI5: J2.1, U12.3
/Relays/Input pins/IN.HI6: J1.9, U10.3
/Relays/Input pins/IN.HI7: J1.7, U8.3
/Relays/Input pins/IN.HI8: J1.5, U6.3
/Relays/Input pins/IN.HI9: J1.3, U4.3
/Relays/Input pins/IN.HI10: J1.1, U2.3
/Relays/Input pins/IN.LO1: J2.10, R61.2, U21.3
/Relays/Input pins/IN.LO2: J2.8, U19.3
/Relays/Input pins/IN.LO3: J2.6, U17.3
/Relays/Input pins/IN.LO4: J2.4, U15.3
/Relays/Input pins/IN.LO5: J2.2, U13.3
/Relays/Input pins/IN.LO6: J1.10, U11.3
/Relays/Input pins/IN.LO7: J1.8, U9.3
/Relays/Input pins/IN.LO8: J1.6, U7.3
/Relays/Input pins/IN.LO9: J1.4, U5.3
/Relays/Input pins/IN.LO10: J1.2, U3.3
/Relays/Input pins/OUT.HI: J3.1, U2.4, U4.4, U6.4, U8.4, U10.4, U12.4, U14.4, U16.4, U18.4, U20.4, U22.3
/Relays/Input pins/OUT.LO: J3.2, U3.4, U5.4, U7.4, U9.4, U11.4, U13.4, U15.4, U17.4, U19.4, U21.4, U23.3
GND: U2.2, U3.2, U4.2, U5.2, U6.2, U7.2, U8.2, U9.2, U10.2, U11.2, U12.2, U13.2, U14.2, U15.2, U16.2, U17.2, U18.2, U19.2, U20.2, U21.2, U22.2, U23.2; also elsewhere on the board
unnamed: R7.1, U2.1
unnamed: R8.1, U3.1
unnamed: R9.1, U4.1
unnamed: R10.1, U5.1
unnamed: R11.1, U6.1
unnamed: R12.1, U7.1
unnamed: R13.1, U8.1
unnamed: R14.1, U9.1
unnamed: R15.1, U10.1
unnamed: R16.1, U11.1
unnamed: R17.1, U12.1
unnamed: R18.1, U13.1
unnamed: R19.1, U14.1
unnamed: R20.1, U15.1
unnamed: R21.1, U16.1
unnamed: R22.1, U17.1
unnamed: R23.1, U18.1
unnamed: R24.1, U19.1
unnamed: R25.1, U20.1
unnamed: R26.1, U21.1
unnamed: R27.1, U22.1
unnamed: R28.1, U23.1

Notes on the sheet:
optional shunt for current measurements
TODO: Replace with SMD TLP3558A(TP1,F
OUT A in the manual

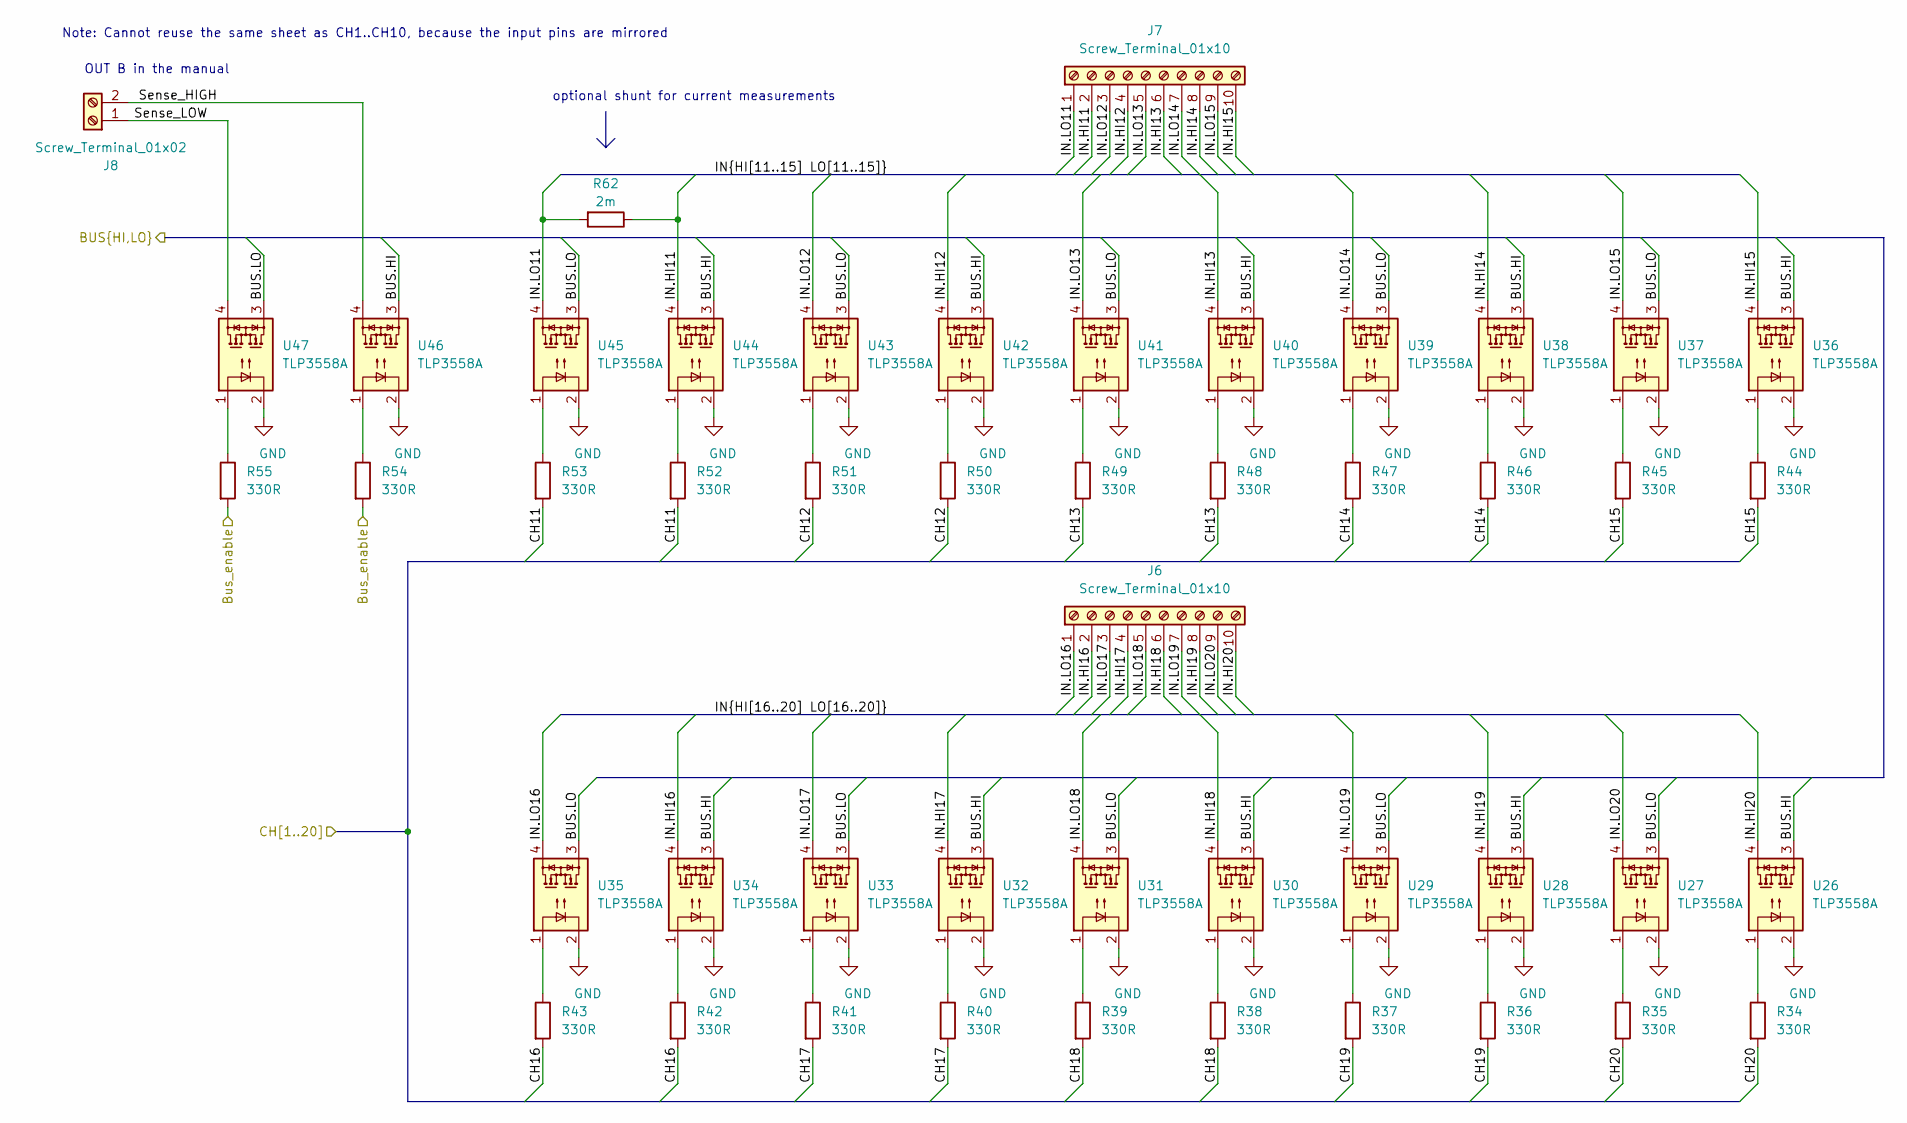
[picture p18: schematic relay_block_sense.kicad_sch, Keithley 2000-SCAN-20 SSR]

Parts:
J6, J7: Screw_Terminal_01x10; TerminalBlock_Phoenix_SMKDSN-1,5-10-5.08_1x10_P5.08mm_Horiz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
J8: Screw_Terminal_01x02; TerminalBlock_Phoenix_SMKDSN-1,5-2-5.08_1x02_P5.08mm_Horizo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
R34, R35, R36, R37, R38, R39, R40, R41, R42, R43, R44, R45, R46, R47, R48, R49, R50, R51, R52, R53, R54, R55: 330R; R_0603_1608Metric
R62: 2m; R_2512_6332Metric
U26, U27, U28, U29, U30, U31, U32, U33, U34, U35, U36, U37, U38, U39, U40, U41, U42, U43, U44, U45, U46, U47: TLP3558A; DIP-4_W7.62mm

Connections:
/FPGA/Bus2_sense_enable: R54.2, R55.2; also elsewhere on the board
/FPGA/CH11: R52.2, R53.2; also elsewhere on the board
/FPGA/CH12: R50.2, R51.2; also elsewhere on the board
/FPGA/CH13: R48.2, R49.2; also elsewhere on the board
/FPGA/CH14: R46.2, R47.2; also elsewhere on the board
/FPGA/CH15: R44.2, R45.2; also elsewhere on the board
/FPGA/CH16: R42.2, R43.2; also elsewhere on the board
/FPGA/CH17: R40.2, R41.2; also elsewhere on the board
/FPGA/CH18: R38.2, R39.2; also elsewhere on the board
/FPGA/CH19: R36.2, R37.2; also elsewhere on the board
/FPGA/CH20: R34.2, R35.2; also elsewhere on the board
/Relays/Input pins/BUS.HI: U26.3, U28.3, U30.3, U32.3, U34.3, U36.3, U38.3, U40.3, U42.3, U44.3, U46.3; also elsewhere on the board
/Relays/Input pins/BUS.LO: U27.3, U29.3, U31.3, U33.3, U35.3, U37.3, U39.3, U41.3, U43.3, U45.3, U47.3; also elsewhere on the board
/Relays/Input/Sense pins/IN.HI11: J7.2, R62.1, U44.4
/Relays/Input/Sense pins/IN.HI12: J7.4, U42.4
/Relays/Input/Sense pins/IN.HI13: J7.6, U40.4
/Relays/Input/Sense pins/IN.HI14: J7.8, U38.4
/Relays/Input/Sense pins/IN.HI15: J7.10, U36.4
/Relays/Input/Sense pins/IN.HI16: J6.2, U34.4
/Relays/Input/Sense pins/IN.HI17: J6.4, U32.4
/Relays/Input/Sense pins/IN.HI18: J6.6, U30.4
/Relays/Input/Sense pins/IN.HI19: J6.8, U28.4
/Relays/Input/Sense pins/IN.HI20: J6.10, U26.4
/Relays/Input/Sense pins/IN.LO11: J7.1, R62.2, U45.4
/Relays/Input/Sense pins/IN.LO12: J7.3, U43.4
/Relays/Input/Sense pins/IN.LO13: J7.5, U41.4
/Relays/Input/Sense pins/IN.LO14: J7.7, U39.4
/Relays/Input/Sense pins/IN.LO15: J7.9, U37.4
/Relays/Input/Sense pins/IN.LO16: J6.1, U35.4
/Relays/Input/Sense pins/IN.LO17: J6.3, U33.4
/Relays/Input/Sense pins/IN.LO18: J6.5, U31.4
/Relays/Input/Sense pins/IN.LO19: J6.7, U29.4
/Relays/Input/Sense pins/IN.LO20: J6.9, U27.4
/Relays/Input/Sense pins/Sense_HIGH: J8.2, U46.4
/Relays/Input/Sense pins/Sense_LOW: J8.1, U47.4
GND: U26.2, U27.2, U28.2, U29.2, U30.2, U31.2, U32.2, U33.2, U34.2, U35.2, U36.2, U37.2, U38.2, U39.2, U40.2, U41.2, U42.2, U43.2, U44.2, U45.2, U46.2, U47.2; also elsewhere on the board
unnamed: R34.1, U26.1
unnamed: R35.1, U27.1
unnamed: R36.1, U28.1
unnamed: R37.1, U29.1
unnamed: R38.1, U30.1
unnamed: R39.1, U31.1
unnamed: R40.1, U32.1
unnamed: R41.1, U33.1
unnamed: R42.1, U34.1
unnamed: R43.1, U35.1
unnamed: R44.1, U36.1
unnamed: R45.1, U37.1
unnamed: R46.1, U38.1
unnamed: R47.1, U39.1
unnamed: R48.1, U40.1
unnamed: R49.1, U41.1
unnamed: R50.1, U42.1
unnamed: R51.1, U43.1
unnamed: R52.1, U44.1
unnamed: R53.1, U45.1
unnamed: R54.1, U46.1
unnamed: R55.1, U47.1

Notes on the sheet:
Note: Cannot reuse the same sheet as CH1..CH10, because the input pins are mirrored
optional shunt for current measurements
OUT B in the manual

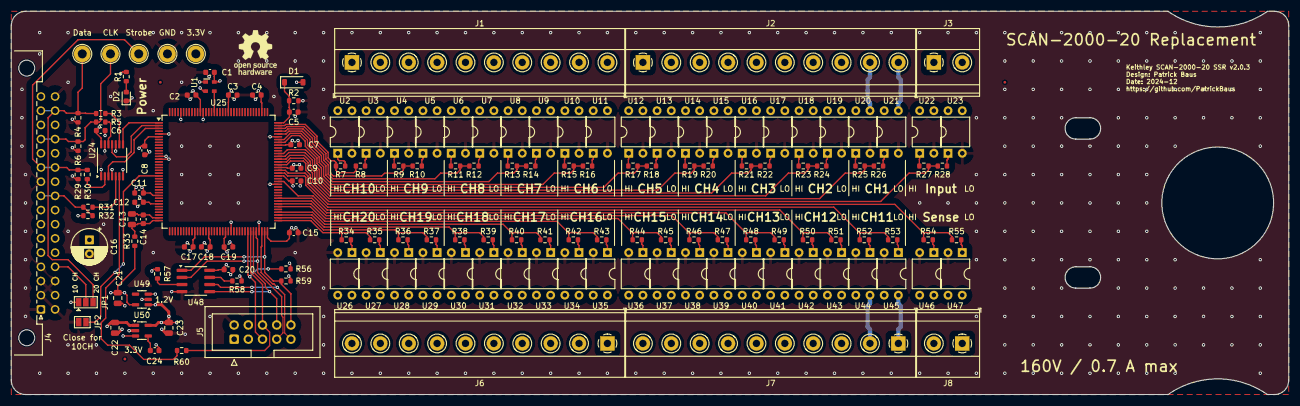
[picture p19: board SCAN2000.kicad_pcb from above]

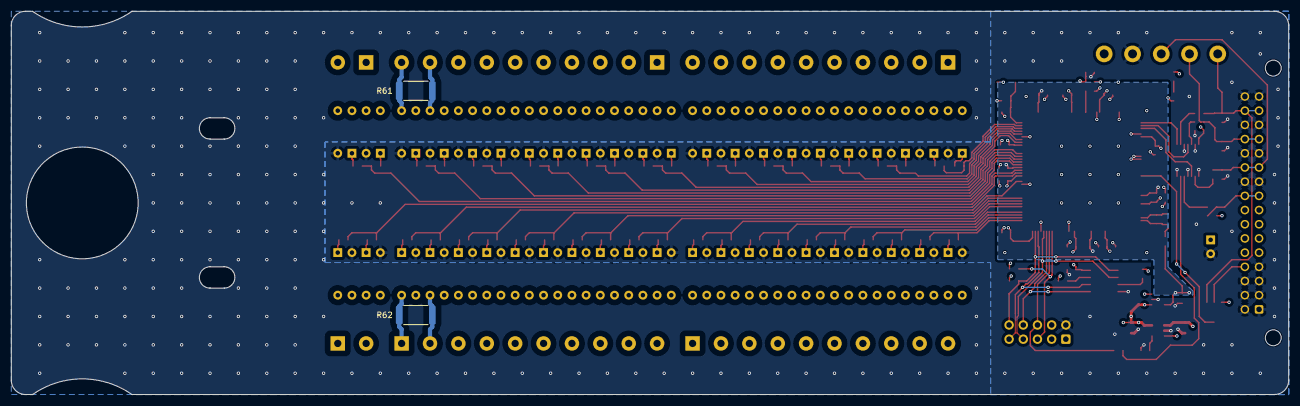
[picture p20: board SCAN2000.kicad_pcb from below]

Board: 4 copper layers, 228.6 x 68.6 mm, 157 parts (2 on the bottom side), 144 nets.

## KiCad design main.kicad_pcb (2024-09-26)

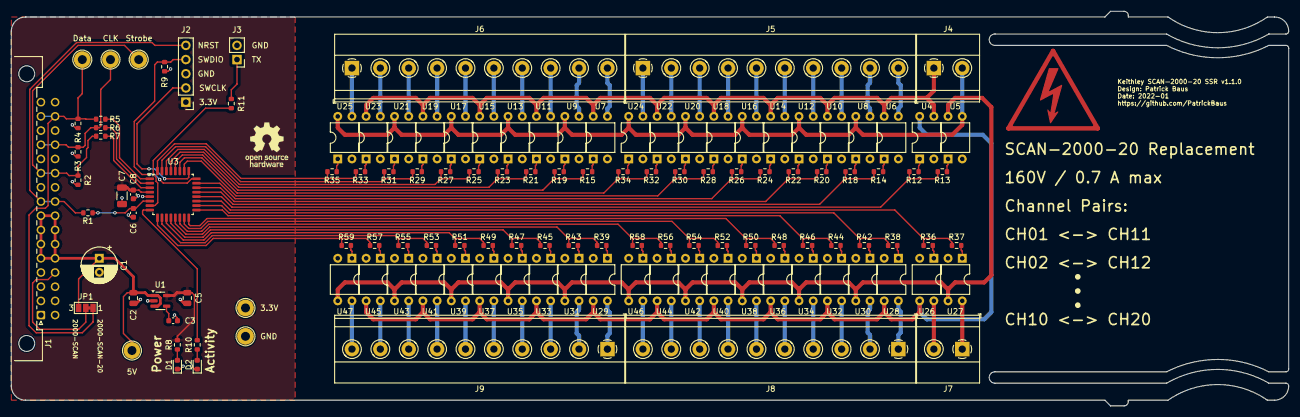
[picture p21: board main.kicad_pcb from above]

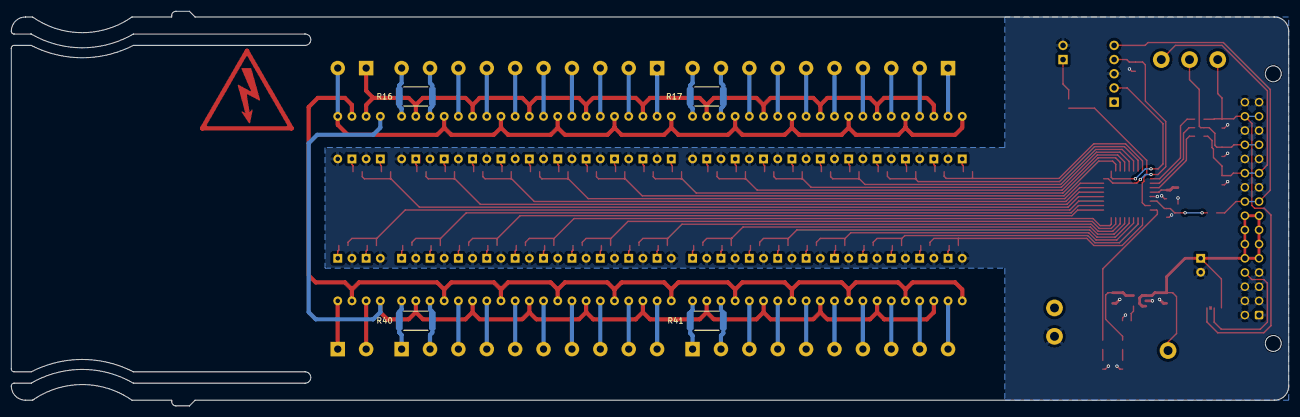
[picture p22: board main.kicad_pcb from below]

Board: 2 copper layers, 228.6 x 70.6 mm, 132 parts (4 on the bottom side), 132 nets.

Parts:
C1: 10u; CP_Radial_D6.3mm_P2.50mm
C2, C5: 1u; C_0805_2012Metric
C3, C6, C8: 100n; C_0603_1608Metric
C7: 4.7u; C_1206_3216Metric
D1, D2: Green; LED_0603_1608Metric
J1: Conn_02x16_Row_Letter_First; DIN41612_B2_2x16_Male_Horizontal_THT
J2: Conn_01x05; PinHeader_1x05_P2.54mm_Vertical
J3: Conn_01x02; PinHeader_1x02_P2.54mm_Vertical
J4, J7: Screw_Terminal_01x02; TerminalBlock_Phoenix_SMKDSN-1,5-2-5.08_1x02_P5.08mm_Horizo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
J5, J6, J8, J9: Screw_Terminal_01x10; TerminalBlock_Phoenix_SMKDSN-1,5-10-5.08_1x10_P5.08mm_Horiz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
JP1: SolderJumper_3_Bridged12; SolderJumper-3_P1.3mm_Bridged12_Pad1.0x1.5mm_NumberLabels
LOGO2: Logo_Open_Hardware_Small; OSHW-Logo_7.5x8mm_SilkScreen
R1, R5, R6, R7, R8, R10, R11, R12, R13, R14, R15, R18, R19, R20, R21, R22, R23, R24, R25, R26, R27, R28, R29, R30, R31, R32, R33, R34, R35, R36, R37, R38, R39, R42, R43, R44, R45, R46, R47, R48, R49, R50, R51, R52, R53, R54, R55, R56, R57, R58, R59: 330R; R_0603_1608Metric
R2, R3, R4, R9: 10k; R_0603_1608Metric
R16, R17, R40, R41: 2m; R_2512_6332Metric
SYM1: SYM_Flash_Small; Symbol_HighVoltage_Triangle_17x15mm_Copper
TP1, TP2, TP3, TP4, TP5, TP6: TestPoint; TestPoint_Loop_D2.60mm_Drill1.6mm_Beaded
U1: TPS73233DBVR; SOT-23-5
U3: STM32G070KBT6; LQFP-32_7x7mm_P0.8mm
U4, U5, U6, U7, U8, U9, U10, U11, U12, U13, U14, U15, U16, U17, U18, U19, U20, U21, U22, U23, U24, U25, U26, U27, U28, U29, U30, U31, U32, U33, U34, U35, U36, U37, U38, U39, U40, U41, U42, U43, U44, U45, U46, U47: TLP3558A; DIP-4_W7.62mm

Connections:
+3V3: C5.1, C7.1, C8.1, J2.1, R8.1, TP2.1, U1.5 (OUT), U3.4 (VDD/VDDA)
+5V: C1.1, C2.1, J1.a5, J1.a6, J1.a7, J1.a8, J1.b5, J1.b6, J1.b7, J1.b8, JP1.3 (B), TP1.1, U1.1 (IN), U1.3 (EN)
/CLK: J1.a13, J1.b13, R3.1, R6.2, TP5.1
/DATA: J1.a15, J1.b15, JP1.1 (A), R4.1, R5.2, TP4.1
/ID: J1.b4, JP1.2 (C)
/Microcontroller/Bus2_input_enable: R12.2, R13.2, U3.20 (PC6)
/Microcontroller/Bus2_sense_enable: R36.2, R37.2, U3.19 (PA9)
/Microcontroller/CH1: R14.2, R18.2, U3.21 (PA10)
/Microcontroller/CH2: R20.2, R22.2, U3.22 (PA11)
/Microcontroller/CH3: R24.2, R26.2, U3.23 (PA12)
/Microcontroller/CH4: R28.2, R30.2, U3.26 (PA15)
/Microcontroller/CH5: R32.2, R34.2, U3.27 (PB3)
/Microcontroller/CH6: R15.2, R19.2, U3.28 (PB4)
/Microcontroller/CH7: R21.2, R23.2, U3.29 (PB5)
/Microcontroller/CH8: R25.2, R27.2, U3.30 (PB6)
/Microcontroller/CH9: R29.2, R31.2, U3.31 (PB7)
/Microcontroller/CH10: R33.2, R35.2, U3.32 (PB8)
/Microcontroller/CH11: R38.2, R42.2, U3.18 (PA8)
/Microcontroller/CH12: R44.2, R46.2, U3.17 (PB2)
/Microcontroller/CH13: R48.2, R50.2, U3.16 (PB1)
/Microcontroller/CH14: R52.2, R54.2, U3.15 (PB0)
/Microcontroller/CH15: R56.2, R58.2, U3.14 (PA7)
/Microcontroller/CH16: R39.2, R43.2, U3.13 (PA6)
/Microcontroller/CH17: R45.2, R47.2, U3.12 (PA5)
/Microcontroller/CH18: R49.2, R51.2, U3.11 (PA4)
/Microcontroller/CH19: R53.2, R55.2, U3.10 (PA3)
/Microcontroller/CH20: R57.2, R59.2, U3.9 (PA2)
/Microcontroller/CLK: R6.1, U3.2 (PC14)
/Microcontroller/DATA: R5.1, U3.1 (PB9)
/Microcontroller/LED: R10.1, U3.8 (PA1)
/Microcontroller/STROBE: R7.1, U3.3 (PC15)
/Microcontroller/SWCLK: J2.2, U3.25 (PA14)
/Microcontroller/SWDIO: J2.4, R9.1, U3.24 (PA13)
/Microcontroller/TX: R11.2, U3.7 (PA0)
/Relays/Input pins/Bus_HIGH: U4.4, U26.3, U28.3, U29.3, U32.3, U33.3, U36.3, U37.3, U40.3, U41.3, U44.3, U45.3
/Relays/Input pins/Bus_LOW: U5.4, U27.3, U30.3, U31.3, U34.3, U35.3, U38.3, U39.3, U42.3, U43.3, U46.3, U47.3
/Relays/Input pins/Out_HIGH: J4.1, U4.3, U6.4, U7.4, U10.4, U11.4, U14.4, U15.4, U18.4, U19.4, U22.4, U23.4
/Relays/Input pins/Out_LOW: J4.2, U5.3, U8.4, U9.4, U12.4, U13.4, U16.4, U17.4, U20.4, U21.4, U24.4, U25.4
/Relays/Input/Sense pins/Sense_HIGH: J7.2, U26.4
/Relays/Input/Sense pins/Sense_LOW: J7.1, U27.4
/STROBE: J1.a11, J1.b11, R2.1, R7.2, TP6.1
/~NRST: J1.a9, J1.b9, J2.5, R1.2
GND: C1.2, C2.2, C3.2, C5.2, C6.2, C7.2, C8.2, D1.1 (K), D2.1 (K), J1.a1, J1.a2, J1.a3, J1.a4, J1.a10, J1.a12, J1.a14, J1.a16, J1.b1, J1.b2, J1.b3, J1.b10, J1.b12, J1.b14, J1.b16, J2.3, J3.2, R2.2, R3.2, R4.2, R9.2, TP3.1, U1.2 (GND), U3.5 (VSS/VSSA), U4.2, U5.2, U6.2, U7.2, U8.2, U9.2, U10.2, U11.2, U12.2, U13.2, U14.2, U15.2, U16.2, U17.2, U18.2, U19.2, U20.2, U21.2, U22.2, U23.2, U24.2, U25.2, U26.2, U27.2, U28.2, U29.2, U30.2, U31.2, U32.2, U33.2, U34.2, U35.2, U36.2, U37.2, U38.2, U39.2, U40.2, U41.2, U42.2, U43.2, U44.2, U45.2, U46.2, U47.2
unnamed: D1.2 (A), R8.2
unnamed: D2.2 (A), R10.2
unnamed: J3.1, R11.1
unnamed: J5.1, U24.3
unnamed: J5.2, U22.3
unnamed: J5.3, U20.3
unnamed: J5.4, U18.3
unnamed: J5.5, U16.3
unnamed: J5.6, U14.3
unnamed: J5.7, U12.3
unnamed: J5.8, U10.3
unnamed: J5.9, R16.1, U8.3
unnamed: J5.10, R16.2, U6.3
unnamed: J6.1, U25.3
unnamed: J6.2, U23.3
unnamed: J6.3, U21.3
unnamed: J6.4, U19.3
unnamed: J6.5, U17.3
unnamed: J6.6, U15.3
unnamed: J6.7, U13.3
unnamed: J6.8, U11.3
unnamed: J6.9, R17.1, U9.3
unnamed: J6.10, R17.2, U7.3
unnamed: J8.1, R40.2, U28.4
unnamed: J8.2, R40.1, U30.4
unnamed: J8.3, U32.4
unnamed: J8.4, U34.4
unnamed: J8.5, U36.4
unnamed: J8.6, U38.4
unnamed: J8.7, U40.4
unnamed: J8.8, U42.4
unnamed: J8.9, U44.4
unnamed: J8.10, U46.4
unnamed: J9.1, R41.2, U29.4
unnamed: J9.2, R41.1, U31.4
unnamed: J9.3, U33.4
unnamed: J9.4, U35.4
unnamed: J9.5, U37.4
unnamed: J9.6, U39.4
unnamed: J9.7, U41.4
unnamed: J9.8, U43.4
unnamed: J9.9, U45.4
unnamed: J9.10, U47.4
unnamed: R12.1, U4.1
unnamed: R13.1, U5.1
unnamed: R14.1, U6.1
unnamed: R15.1, U7.1
unnamed: R18.1, U8.1
unnamed: R19.1, U9.1
unnamed: R20.1, U10.1
unnamed: R21.1, U11.1
unnamed: R22.1, U12.1
unnamed: R23.1, U13.1
unnamed: R24.1, U14.1
unnamed: R25.1, U15.1
unnamed: R26.1, U16.1
unnamed: R27.1, U17.1
unnamed: R28.1, U18.1
unnamed: R29.1, U19.1
unnamed: R30.1, U20.1
unnamed: R31.1, U21.1
unnamed: R32.1, U22.1
unnamed: R33.1, U23.1
unnamed: R34.1, U24.1
unnamed: R35.1, U25.1
unnamed: R36.1, U26.1
unnamed: R37.1, U27.1
unnamed: R38.1, U28.1
unnamed: R39.1, U29.1
unnamed: R42.1, U30.1
unnamed: R43.1, U31.1
unnamed: R44.1, U32.1
unnamed: R45.1, U33.1
unnamed: R46.1, U34.1
unnamed: R47.1, U35.1
unnamed: R48.1, U36.1
unnamed: R49.1, U37.1
unnamed: R50.1, U38.1
unnamed: R51.1, U39.1
unnamed: R52.1, U40.1
unnamed: R53.1, U41.1
unnamed: R54.1, U42.1
unnamed: R55.1, U43.1
unnamed: R56.1, U44.1
unnamed: R57.1, U45.1
unnamed: R58.1, U46.1
unnamed: R59.1, U47.1
unnamed: C3.1, U1.4 (NR)
unnamed: C6.1, R1.1, U3.6 (NRST)

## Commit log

2022-01-11 Replaced Picoblade connector with standard pin header Updated libraries to KiCAD 6 format
    [main-B_Cu.gbr, main-B_Fab.gbr, main-B_Mask.gbr, main-B_Paste.gbr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]
2022-01-11 Updated PCB picture to latest version
2022-01-15 Updated documentation
    [main.kicad_sch, relay_block.kicad_sch, relay_block_sense.kicad_sch]
2022-01-17 Updated silkscreen
    [main.kicad_pcb, main.kicad_sch, mcu.kicad_sch]
2022-01-17 Updated BOM
    [main.kicad_pcb, main.kicad_sch, main_bom_v.1.1.0.csv, mcu.kicad_sch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]
2022-01-31 Added screenshots of the serial data
    [K2002_commands_and_second_transmitter.csv, mcu.kicad_sch]
2024-09-26 Updated to KiCad 8 (#1)
    - Updated libraries
    - Updated BOM, replaced obsolete parts
    [main.kicad_pcb, main.kicad_sch, mcu.kicad_sch, relay_block.kicad_sch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]
2024-09-26 Add CI script (#2)
    * Renamed main files to SCAN2000
    * Add CI
    * Bump version to 1.1.1
    * Remove the BOM as this is now generated content
    * Reworked Readme
    [SCAN2000.kicad_pcb, SCAN2000.kicad_sch, main_bom_v.1.1.0.csv, mcu.kicad_sch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]
2024-09-26 Removed gerber files
    [main-B_Cu.gbr, main-B_Fab.gbr, main-B_Mask.gbr, main-B_Paste.gbr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]
2024-09-26 Moved serial protocol logs to separate folder
    [K2002_commands_and_second_transmitter.csv]
2024-09-26 Updated version string
    [SCAN2000.kicad_pcb, SCAN2000.kicad_sch, mcu.kicad_sch, relay_block.kicad_sch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]
2024-10-11 Replace the STM32 with an iCE40 FPGA (#3)
    * Replaced the STM32 microcontroller with an iCE40 FPGA
    * Bump version to 2.0.2, because of the update to KiCad 8
    * Updated BOM properties
    * Updated PCB image
    * Updated readme for the FPGA version
    * Updated links
    [SCAN2000.kicad_pcb, SCAN2000.kicad_sch, fpga.kicad_sch, mcu.kicad_sch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]
2024-11-26 Add serial protocol doc (#5)
    * Moved serial protocol documentation to doc/
    * Added plot scripts and configs
    [DMM6500-SCAN2000-20_close_CH1.csv, DMM6500-SCAN2000-20_close_CH10_4W.csv, DMM6500-SCAN2000-20_close_CH1_4W.csv, DMM6500-SCAN2000-20_close_CH20.csv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]
2024-12-12 Added missing layers In1.CU and In2.Cu to the CI. (#7)
    * Added missing layers In1.CU and In2.Cu to the CI. This fixes #6.
    * Bump version to 2.0.3
    [SCAN2000.kicad_pcb, SCAN2000.kicad_sch, fpga.kicad_sch, relay_block.kicad_sch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]

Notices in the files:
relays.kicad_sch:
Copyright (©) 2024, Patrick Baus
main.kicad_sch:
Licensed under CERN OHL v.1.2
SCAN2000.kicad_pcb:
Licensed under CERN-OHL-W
